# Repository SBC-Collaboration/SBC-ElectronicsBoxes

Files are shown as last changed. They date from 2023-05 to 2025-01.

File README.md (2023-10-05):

This repository contains KiCAD drawings for the LED driver PCB design, LED driver box connections, and DIO box connections. It also has the SolidWorks drawings for the panel cutouts in those boxes for CNC machining.

## LED driver
This PCB design is for driving the LED rings at 100FPS with 1A current. Each board will be able to drive 20 IR LEDs (LZ1-00R402-0000) in series. The wiring into the PCB is connectorized, so if a board fails, it can be fixed by plugging into the backup board. The op-amp is also installed onto a DIP8 daughter board, so switching a burned-out op-amp does not require soldering in the box. 
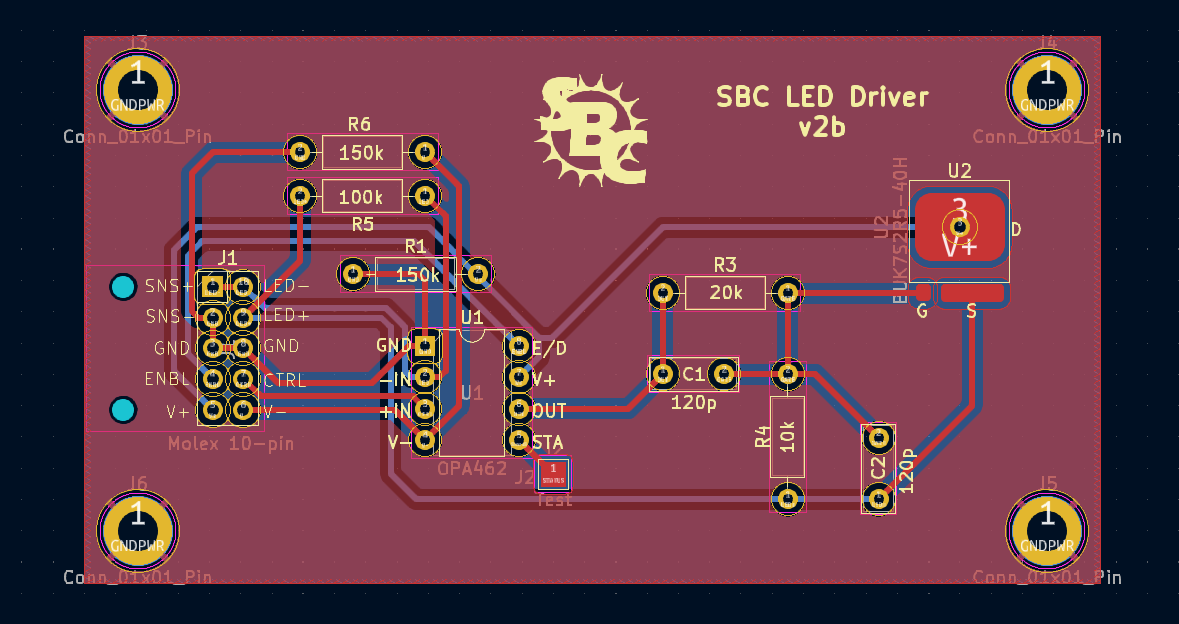
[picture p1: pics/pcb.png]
LED driver PCB

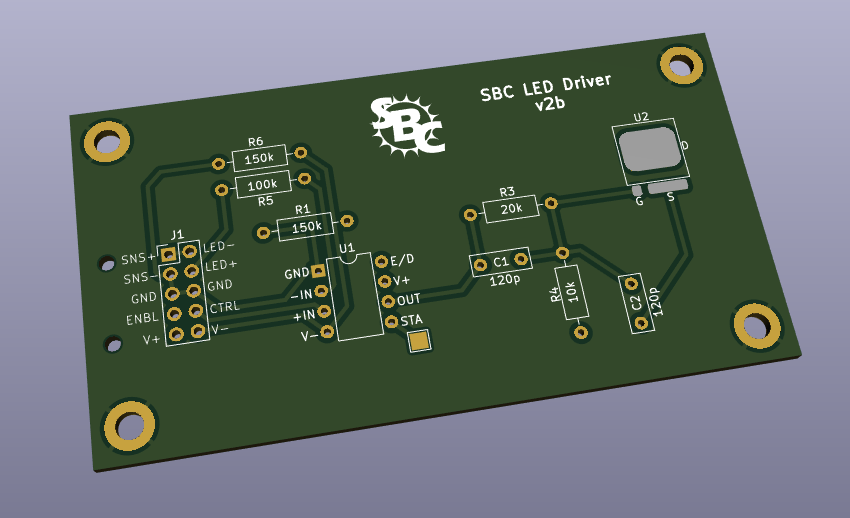
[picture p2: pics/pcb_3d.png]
LED driver PCB 3D


## LED driver box
Three PCB boards drive one LED ring, consisted of 57 LEDs total (19 in each segment). There are three sets of boards in the box, corresponding to three LED rings, plus one backup board. Three 48V 3A power supplies each power one LED ring (three boards). Clock signals from the DIO box and the control voltage pins from the PLC go through DB15 and DB9 connectors, respectively. All digital grounds are connected together, but not necessarily shared with the chassis ground (because of the painted panels). Each LED segment is connected in series with a 1 Ohm power resistor that can be used to sense the current, and also protects the LEDs inside the chamber. On the back, each LED uses a 6-pin amphenol connector, one power and one return pins for each of the LED segments. 

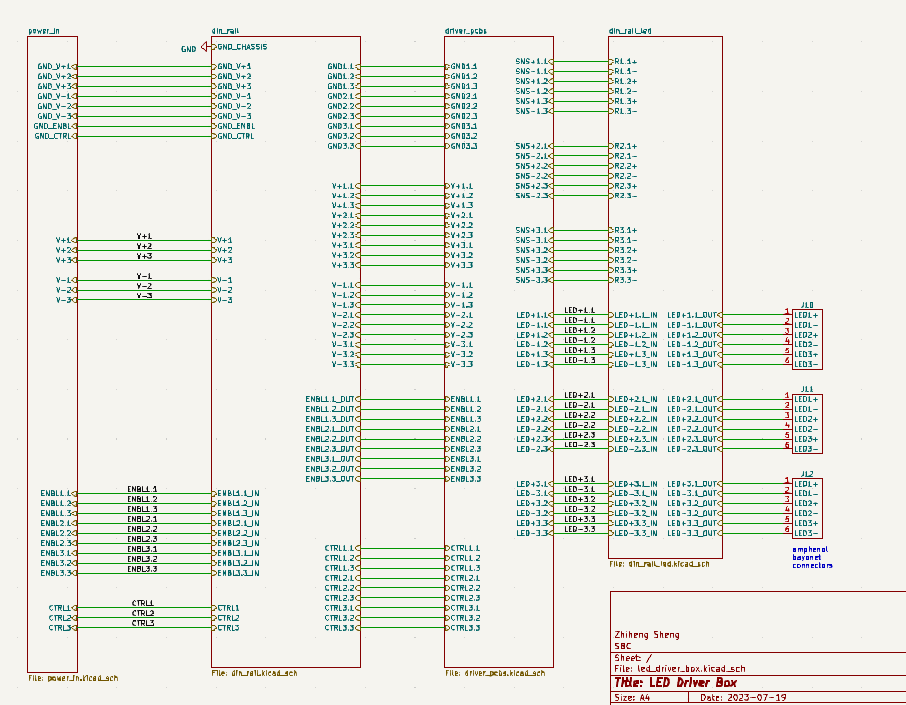
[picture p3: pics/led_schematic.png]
LED box schematics

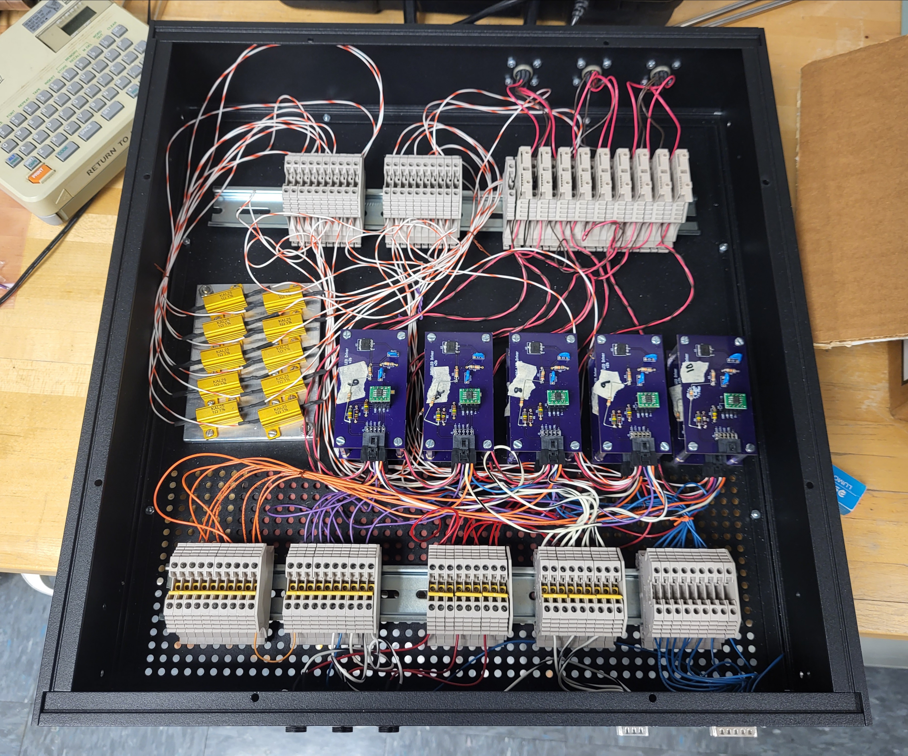
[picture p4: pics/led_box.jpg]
LED box

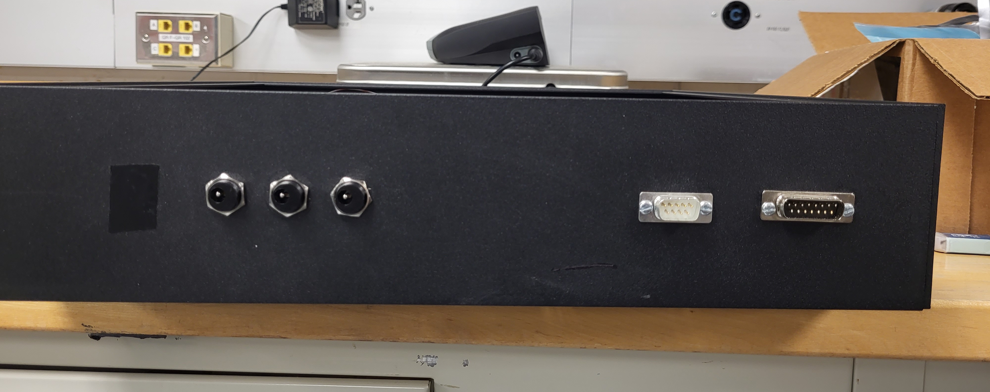
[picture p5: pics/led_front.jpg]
LED box front panel

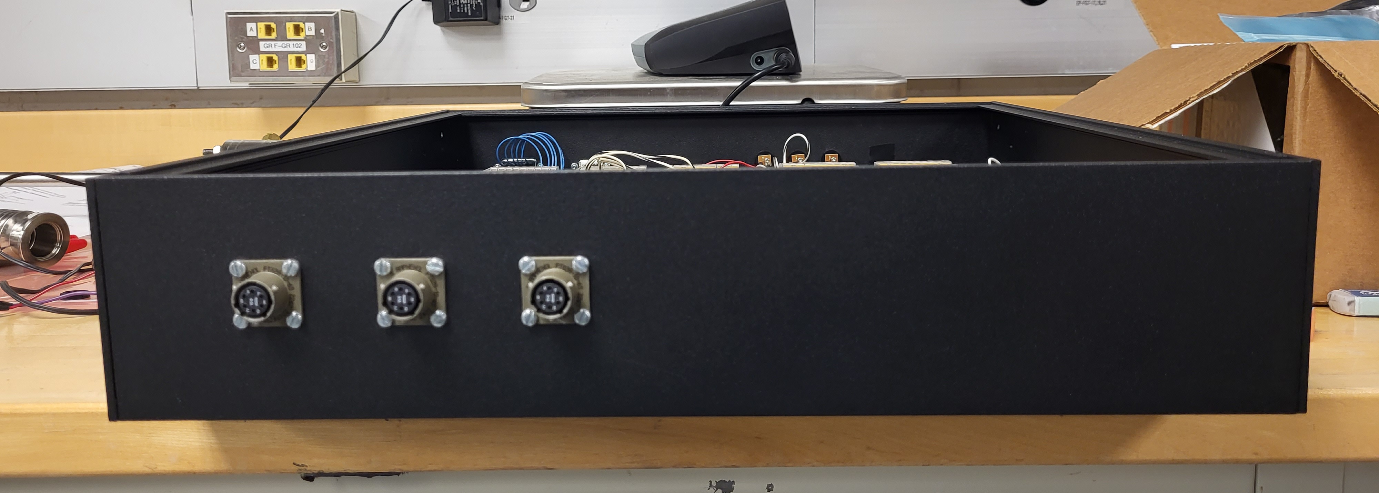
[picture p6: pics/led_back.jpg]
LED box back panel


## Digital I/O box
The DIO box is the central hub for all logic signals, including triggers, clocks, and camera controls. The back panel has four power supply jacks, each rated for 5V 3A. Three are passed through DB9s on the front panel to power the RPis for cameras, and one is used to power the USB hub. A USB jack on the back is connected to the hub, which in turn powers the three Arduinos and one NI USB device. One Arduino is responsible for trigger fan-in/fan-out. It takes trigger in and out from the 16 lemo connectors and the three camera DB9s on the front, as well as through the PLC DB9 on the back, and from the NI device from run control. The trigger reset signal comes from the NI device as well. THe clock Arduino sends clock out through the camera clock DB9 on the back, and also LED DB15 on the front. Another Ethernet jack is plugged into the ethernet shield on the Arduino for bellow position sensing. Two lemo connectors with isolated grounds are used for the sensing line for the position sensor, while the pulse signals are sent through the PLC DB9. Inside the box all digital grounds are connected together, and logic level converter or voltage divider is used for converting voltage between 3.3V(RPi), 5V (NI,Arduino,etc), and 24V (PLC). 

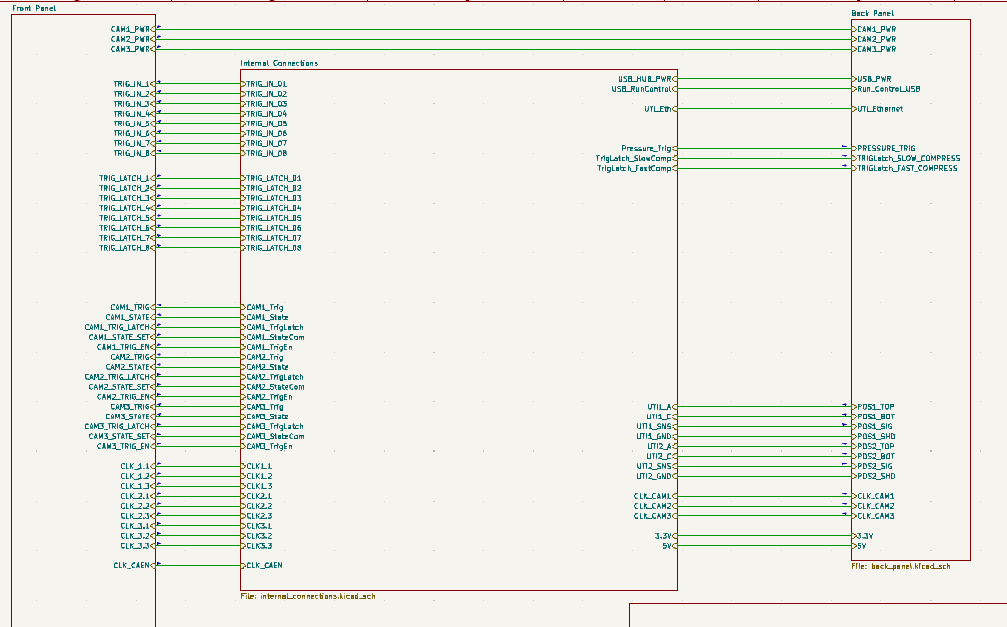
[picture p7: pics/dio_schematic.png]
DIO box schematic

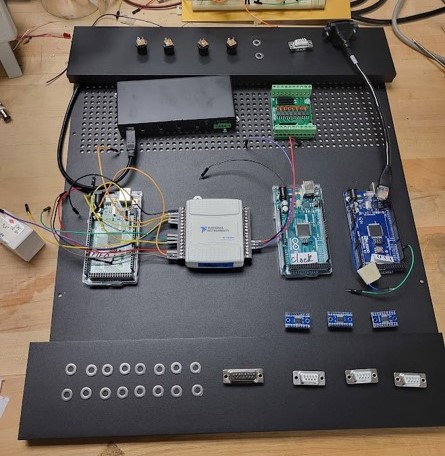
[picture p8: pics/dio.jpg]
DIO box


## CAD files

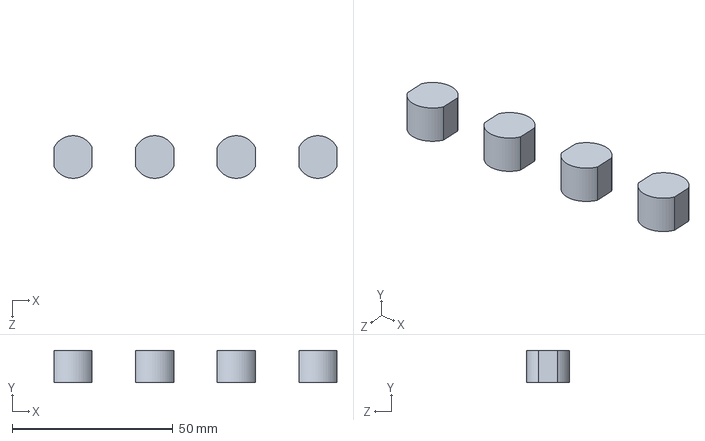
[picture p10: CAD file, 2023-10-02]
connector cutouts/barrel_dio.SLDASM
88.1 x 10.0 x 13.3 mm
barrel x 4

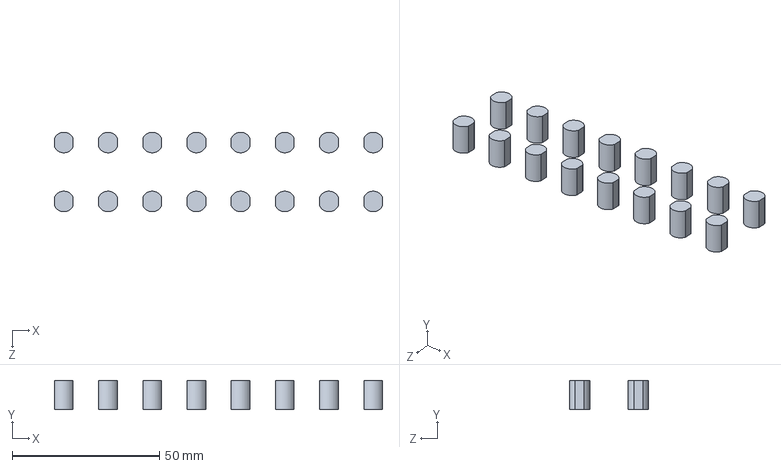
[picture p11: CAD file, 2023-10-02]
connector cutouts/lemo_cutouts.SLDASM
111.4 x 10.0 x 27.0 mm
lemo x 16

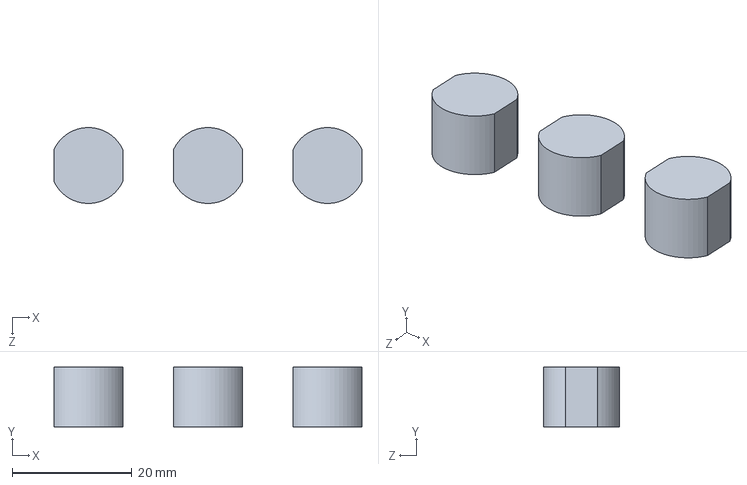
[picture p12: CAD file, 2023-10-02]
connector cutouts/barrel assem.SLDASM
51.5 x 10.0 x 12.7 mm
barrel x 3

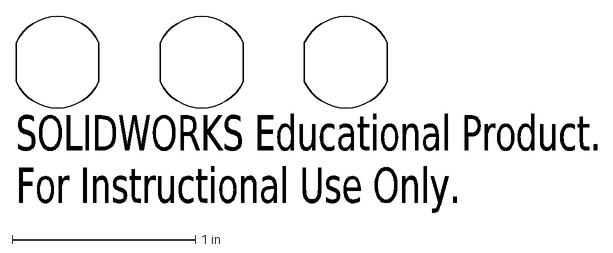
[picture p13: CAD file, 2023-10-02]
connector cutouts/CNC drawings/barrelinch.DXF
SOLIDWORKS Educational Product.
For Instructional Use Only.

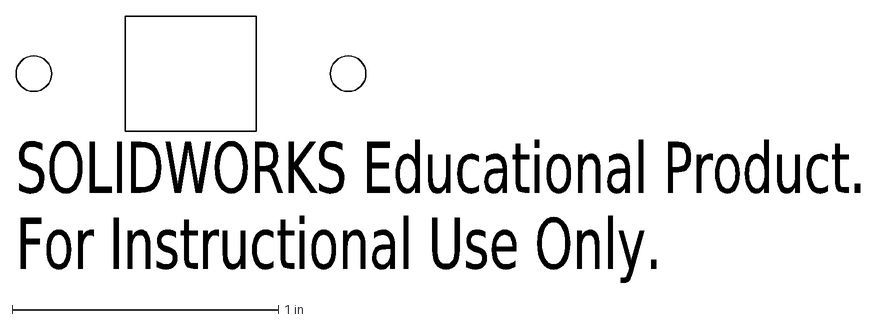
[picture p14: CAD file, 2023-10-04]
connector cutouts/DIO CNC/USBin.DXF
SOLIDWORKS Educational Product.
For Instructional Use Only.

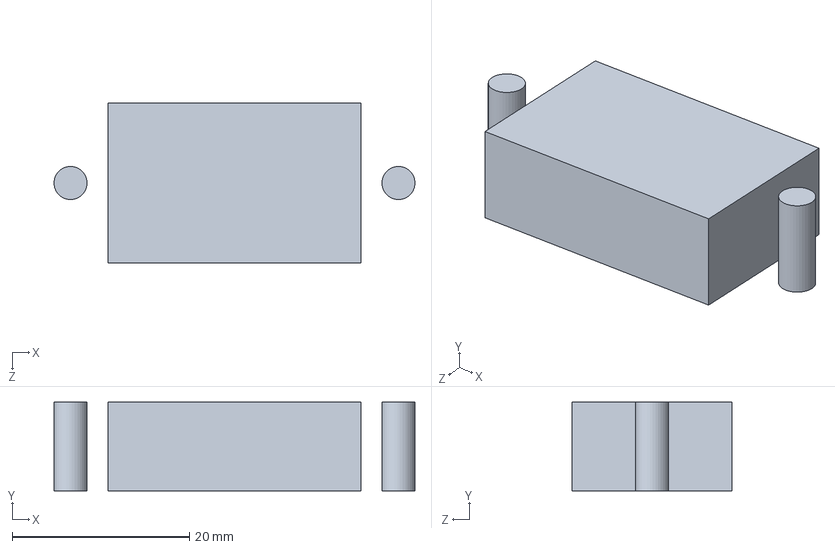
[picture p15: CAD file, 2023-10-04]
connector cutouts/Eth connector.SLDPRT
40.7 x 10.0 x 18.0 mm

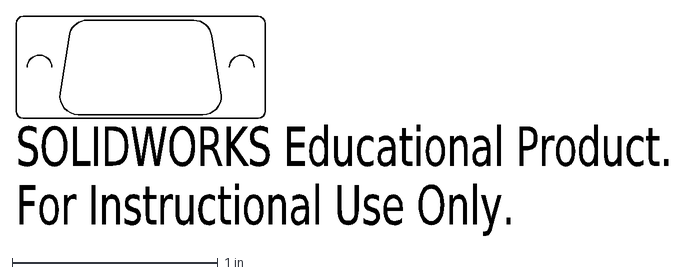
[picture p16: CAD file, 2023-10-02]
connector cutouts/CNC drawings/db9reverseinch.DXF
SOLIDWORKS Educational Product.
For Instructional Use Only.

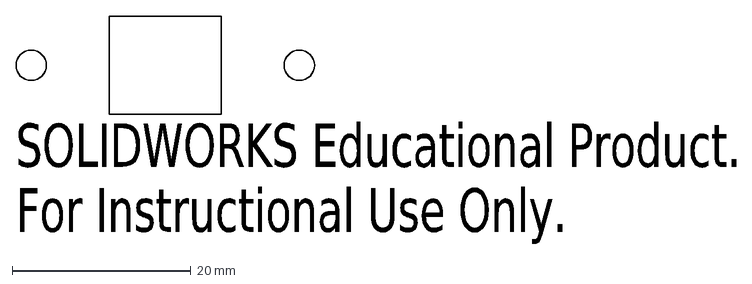
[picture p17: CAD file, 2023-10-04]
connector cutouts/DIO CNC/USBmm.DXF
SOLIDWORKS Educational Product.
For Instructional Use Only.

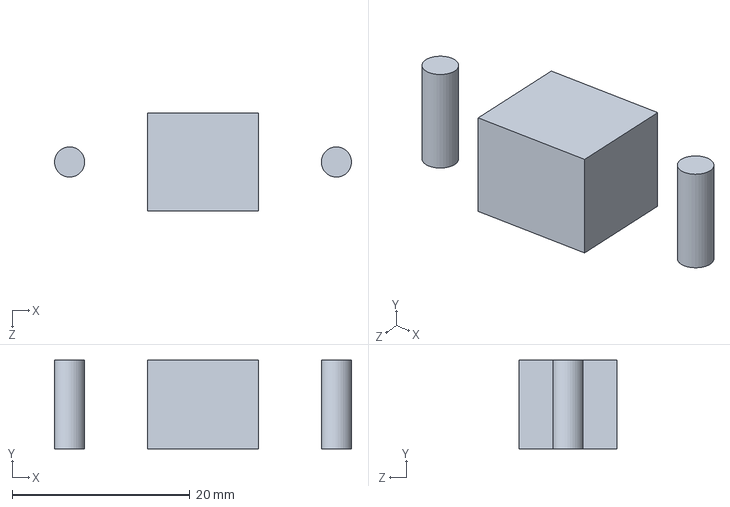
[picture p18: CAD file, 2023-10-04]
connector cutouts/USB connector.SLDPRT
33.4 x 10.0 x 11.0 mm

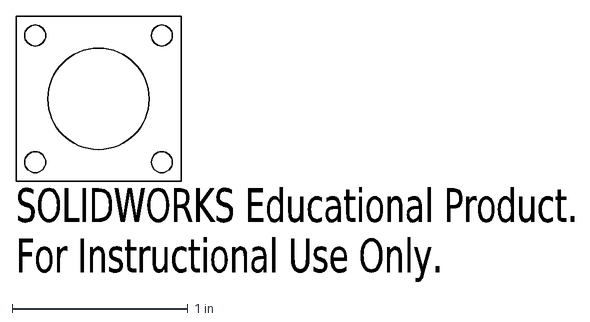
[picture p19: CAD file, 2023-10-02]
connector cutouts/CNC drawings/amphenol inch.DXF
SOLIDWORKS Educational Product.
For Instructional Use Only.

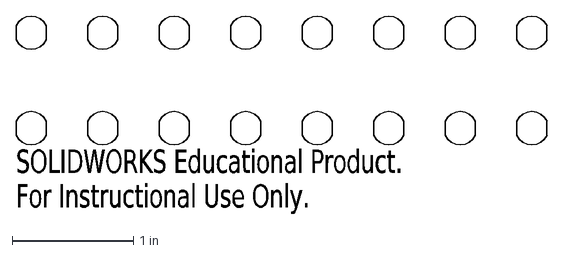
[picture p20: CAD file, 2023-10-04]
connector cutouts/DIO CNC/lemo_in.DXF
SOLIDWORKS Educational Product.
For Instructional Use Only.

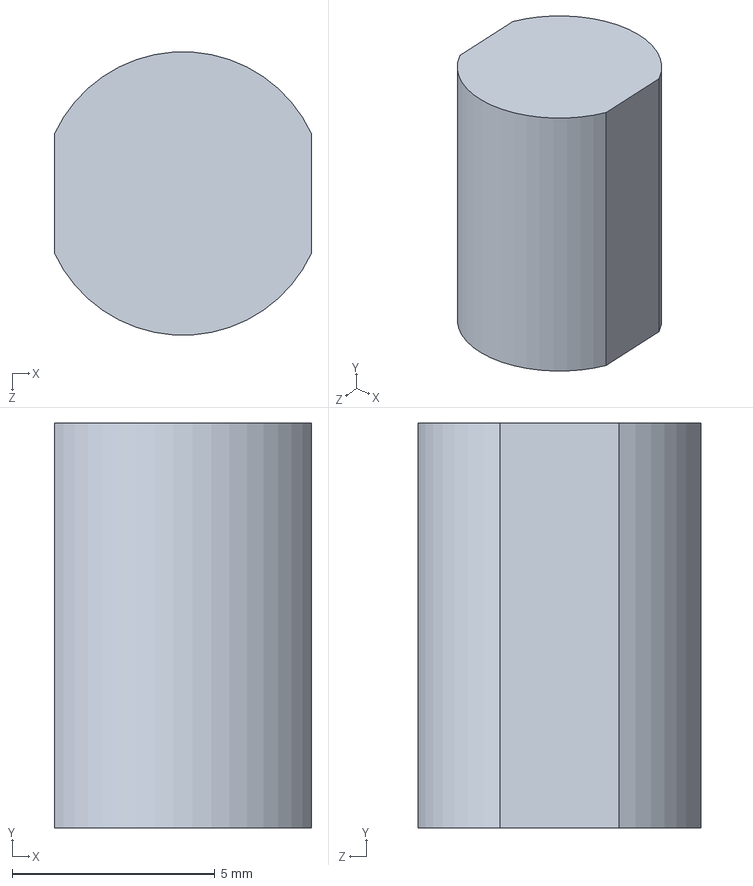
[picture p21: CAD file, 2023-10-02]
connector cutouts/lemo.SLDPRT
6.35 x 10.0 x 6.98 mm

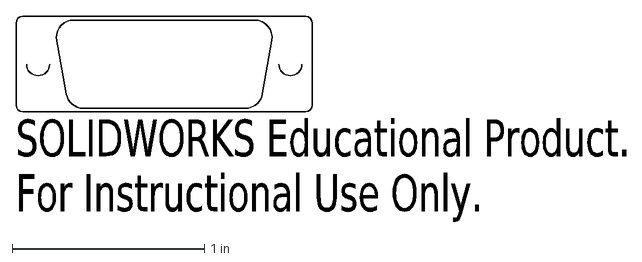
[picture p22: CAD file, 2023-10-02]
connector cutouts/CNC drawings/db15inch.DXF
SOLIDWORKS Educational Product.
For Instructional Use Only.

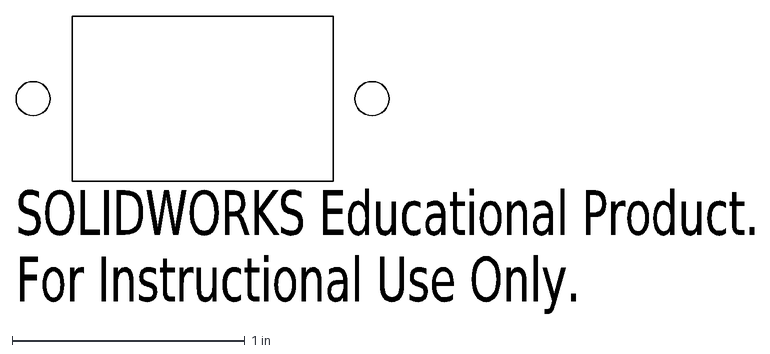
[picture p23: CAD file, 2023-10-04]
connector cutouts/DIO CNC/ETH_in.DXF
SOLIDWORKS Educational Product.
For Instructional Use Only.

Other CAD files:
connector cutouts/CNC drawings/db9reverse.DXF
connector cutouts/DIO CNC/ETH_mm.DXF
connector cutouts/barrel.SLDPRT
connector cutouts/CNC drawings/db15reverse.DXF
connector cutouts/171-009-103.STEP
connector cutouts/171-009-103.step.SLDPRT
connector cutouts/171-015-103.SLDPRT
connector cutouts/171-015-103.STEP
connector cutouts/CNC drawings/171-009-103.step.DXF
connector cutouts/CNC drawings/171-015-103.DXF
connector cutouts/CNC drawings/barrels.DXF
connector cutouts/CNC drawings/db9inch.DXF
connector cutouts/CNC drawings/three amphenol inch.DXF
connector cutouts/DIO CNC/barrel_dio_in.DXF
connector cutouts/DIO CNC/barrel_dio_mm.DXF
connector cutouts/DIO CNC/lemo_mm.DXF
connector cutouts/amphenol cutout.SLDPRT
connector cutouts/barrel assem.SLDPRT
connector cutouts/barrel assem_old.SLDPRT
connector cutouts/barrel_dio.SLDPRT
connector cutouts/barrel_old.SLDPRT
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

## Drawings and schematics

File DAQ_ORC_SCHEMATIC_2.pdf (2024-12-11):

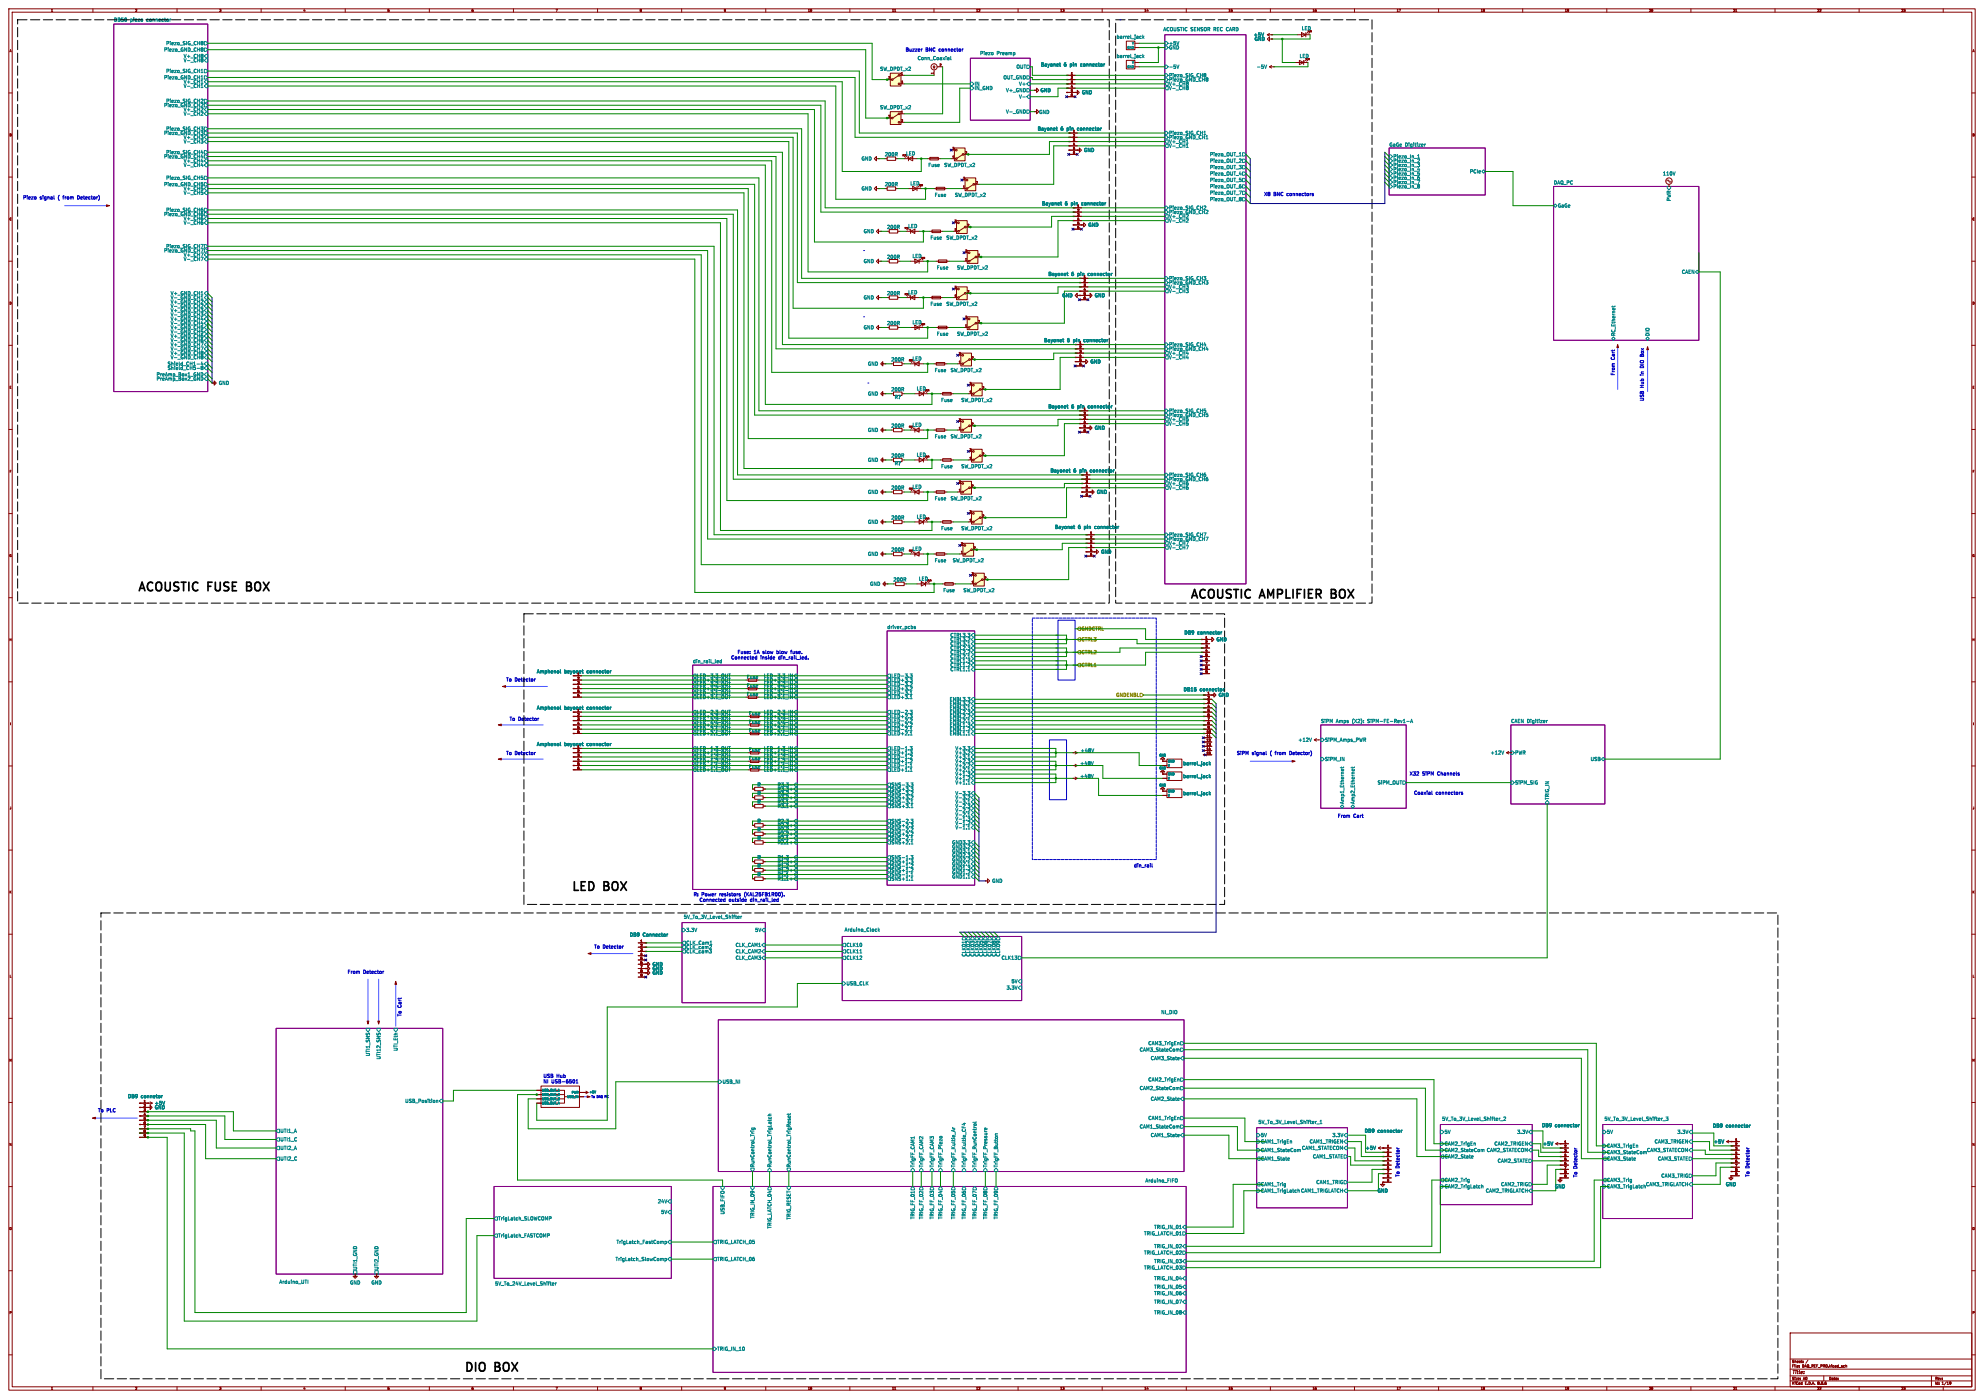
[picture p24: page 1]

ACOUSTIC SENSOR REC CARD

LED 123456 Bayonet 6 pin connector

X8 BNC connectors To Cart

Piezo signal ( from Detector)

GND 123456 Bayonet 6 pin connector

GND 123456 Bayonet 6 pin connector RR

Fuse: 1A slow blow fuse.
Connected inside din_rail_led.

Fuse 123456 Amphenol beyonet connector

Fuse 123456 Amphenol beyonet connector 123456 Amphenol beyonet connector

GND V GND GND GND Amphenol beyonet connector 123456 Amphenol beyonet connector 123456

SiPM Amps (X2): SiPM-FE-Rev1-A

SiPM signal ( from Detector)

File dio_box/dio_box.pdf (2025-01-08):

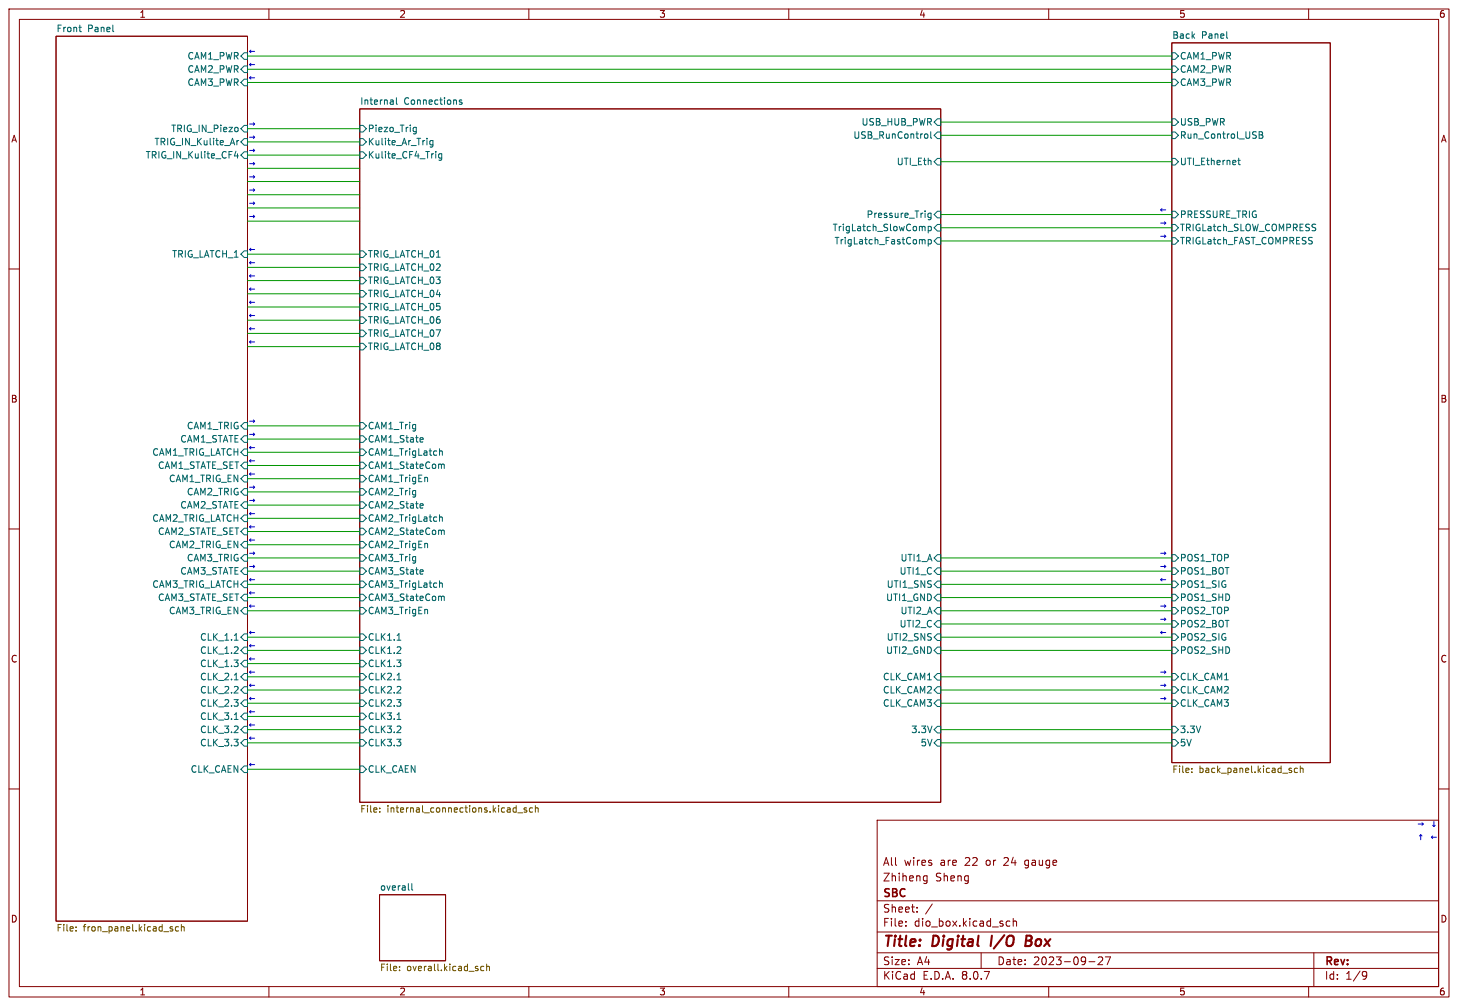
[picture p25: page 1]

Zhiheng Sheng All wires are 22 or 24 gauge

Id: 1/9 Title: Digital I/O Box

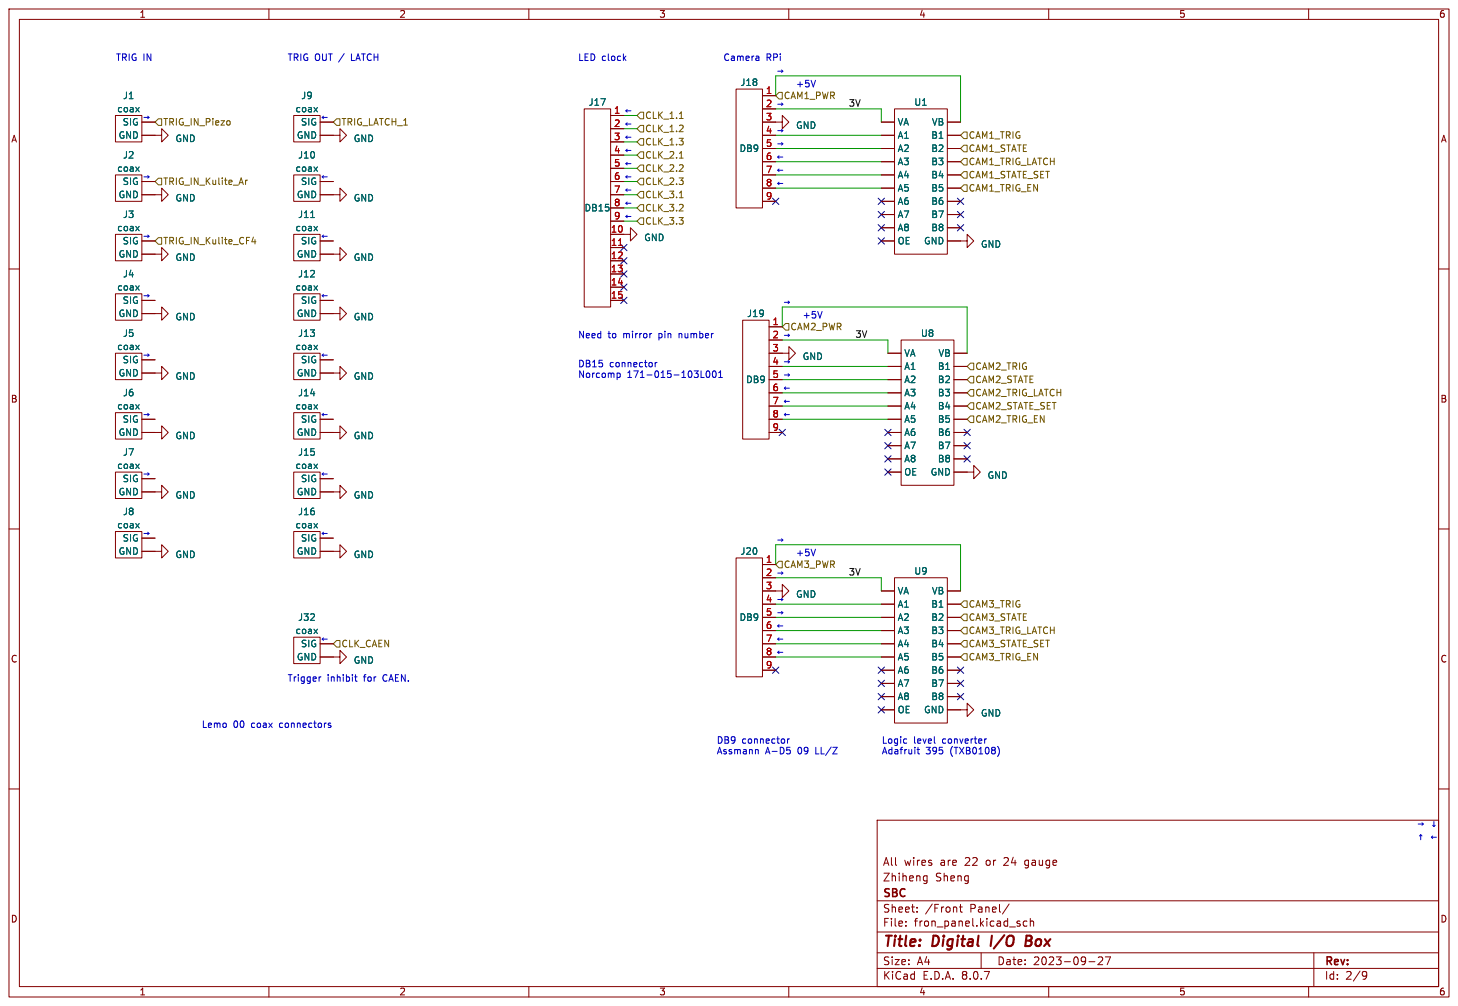
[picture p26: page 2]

þÿ!• LED clockþÿ!•
þÿ!’ DB9 connector Assmann A-D5 09 LL/Z

SIG
Zhiheng Sheng All wires are 22 or 24 gauge GND GND GND
GND

Id: 2/9 Title: Digital I/O Box

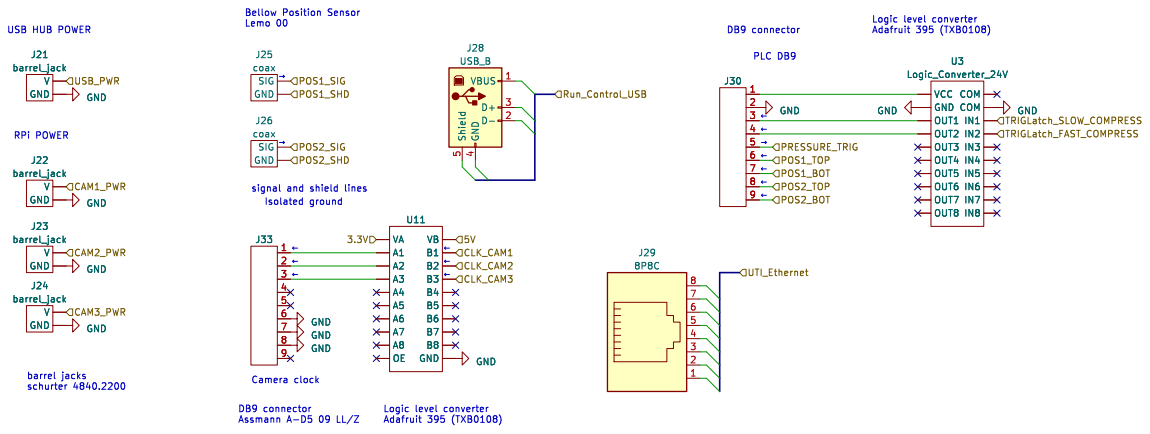
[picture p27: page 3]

þÿ!• DB9 connector þÿ!• RPi POWER

Logic level converter Adafruit 395 (TXB0108)
þÿ!• PLC DB9

þÿ!‘þÿ!• DB9 connector Assmann A-D5 09 LL/Z Camera clock þÿ!•

Zhiheng Sheng All wires are 22 or 24 gauge

Id: 3/9 Title: Digital I/O Box

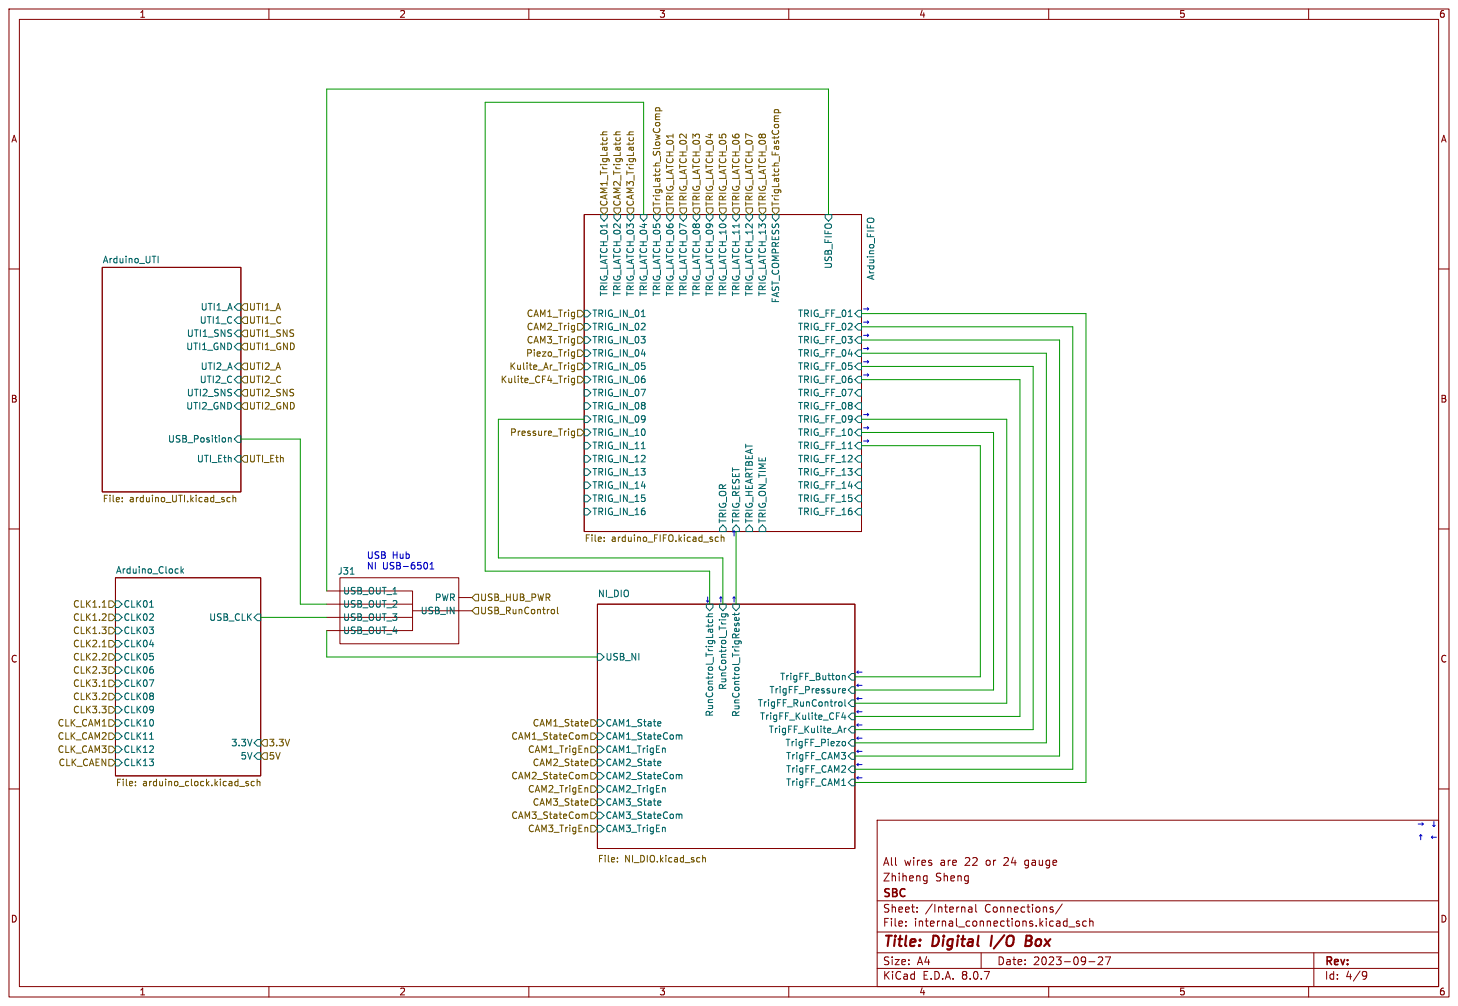
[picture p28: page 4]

þÿ!’ USB Hub NI USB-6501

Id: 4/9 Title: Digital I/O Box

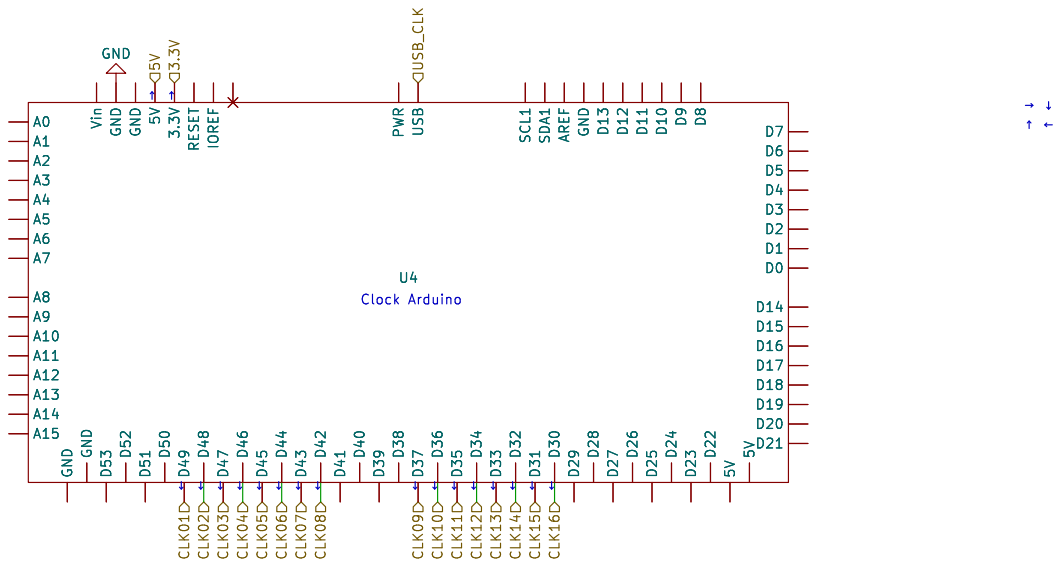
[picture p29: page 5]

þÿ!“þÿ!“ Clock Arduino

Zhiheng Sheng All wires are 22 or 24 gauge

Id: 5/9 Title: Digital I/O Box

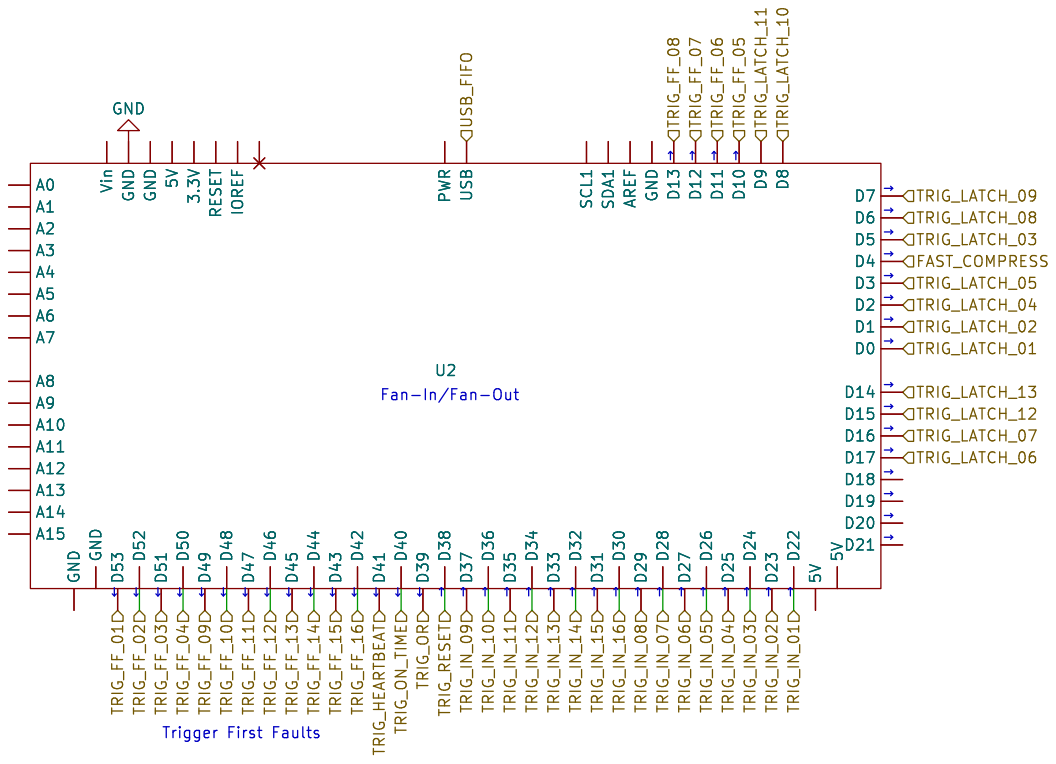
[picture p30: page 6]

Trigger First Faults þÿ!“þÿ!“

Zhiheng Sheng All wires are 22 or 24 gauge

Id: 6/9 Title: Digital I/O Box

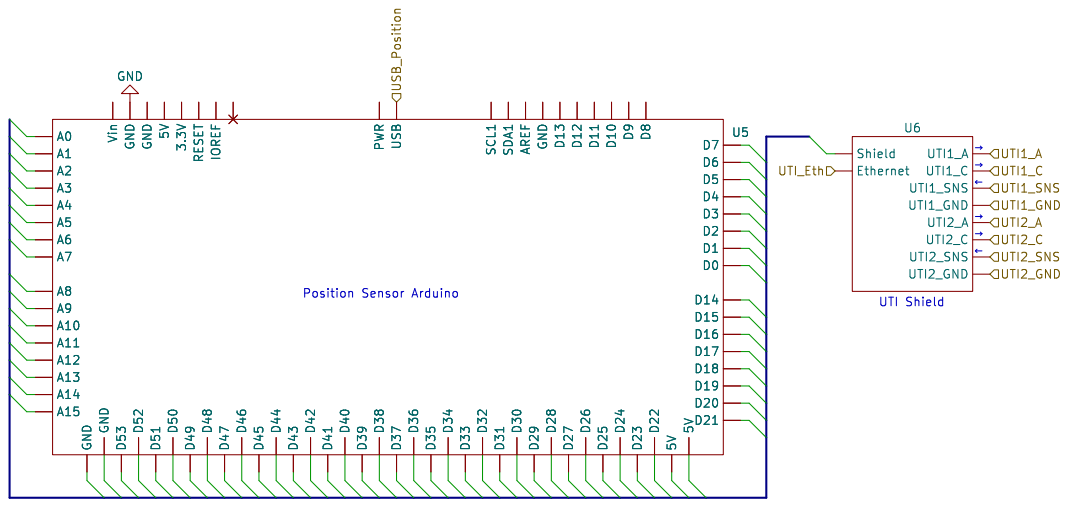
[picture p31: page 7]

Zhiheng Sheng All wires are 22 or 24 gauge

Id: 7/9 Title: Digital I/O Box

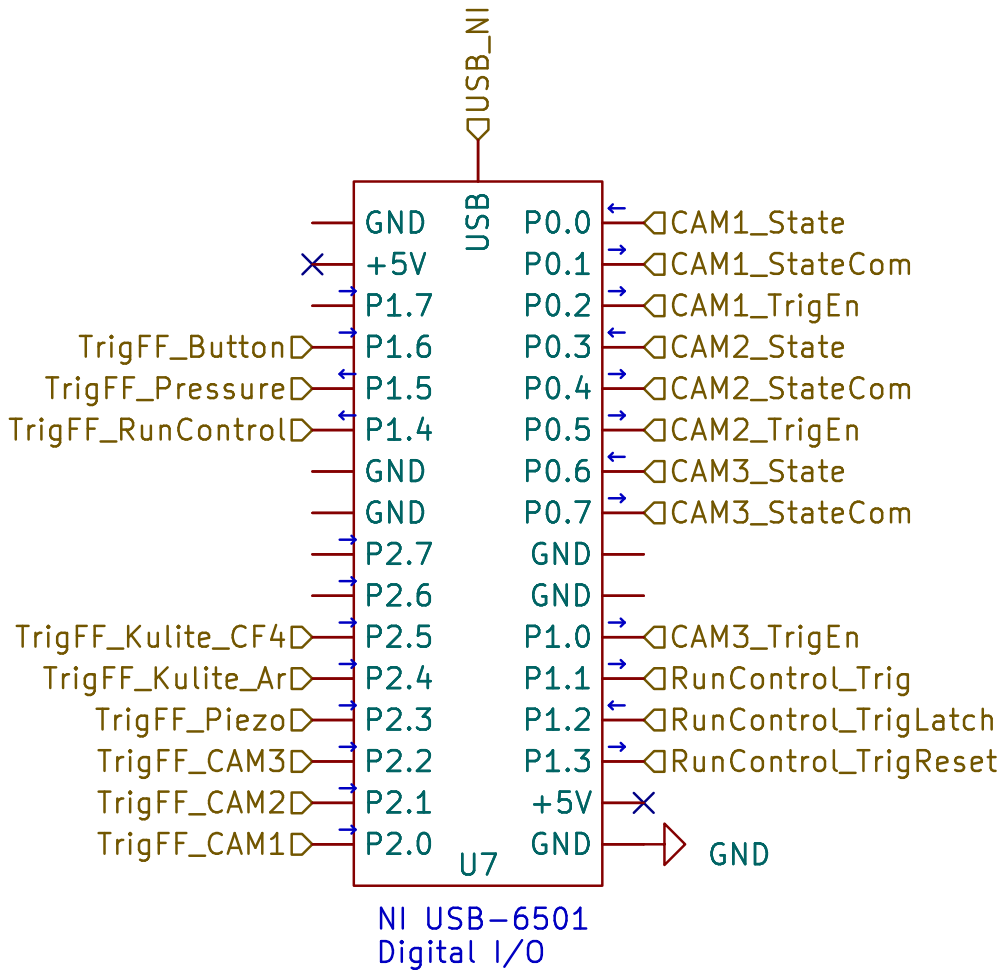
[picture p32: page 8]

Zhiheng Sheng All wires are 22 or 24 gauge

Id: 8/9 Title: Digital I/O Box

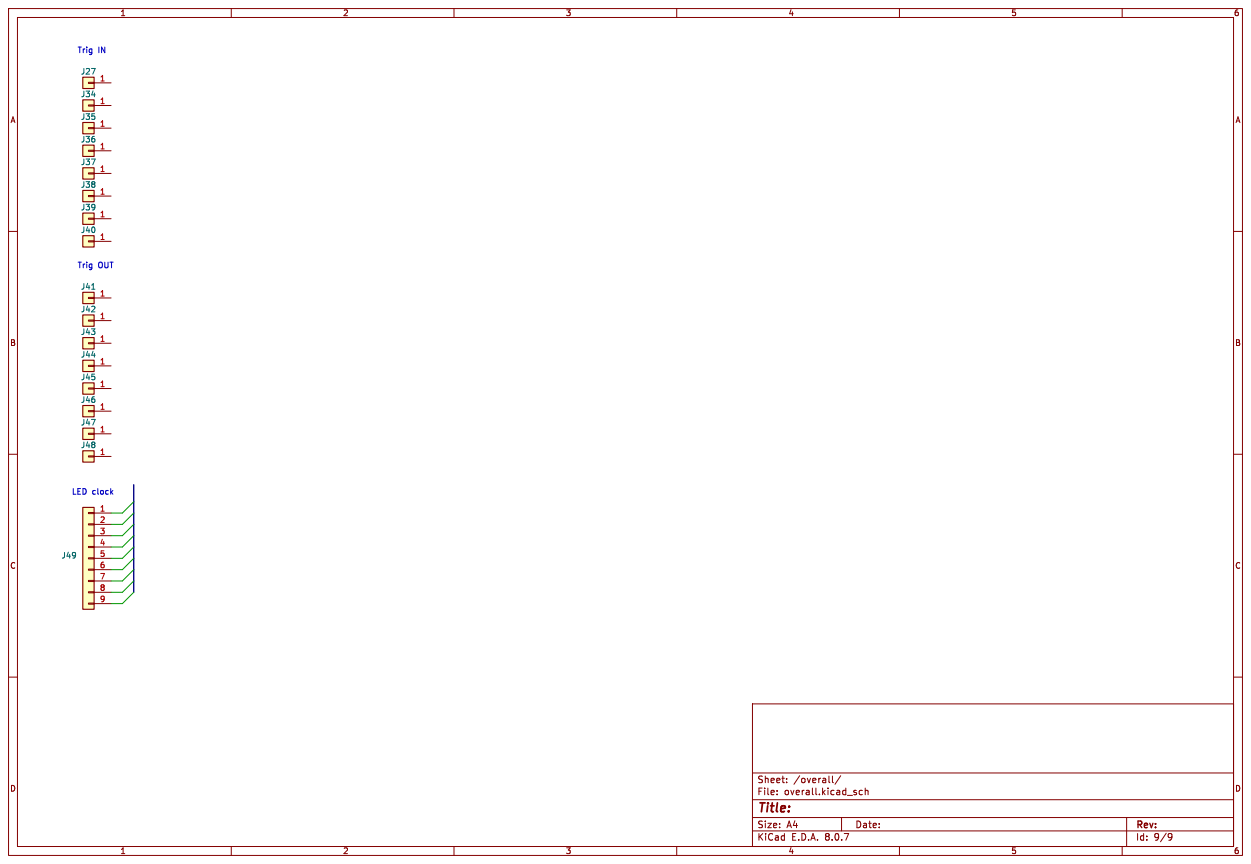
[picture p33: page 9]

Trig IN
LED clock Trig OUT

Id: 9/9 Title: File: overall.kicad_sch Sheet: /overall/ 1

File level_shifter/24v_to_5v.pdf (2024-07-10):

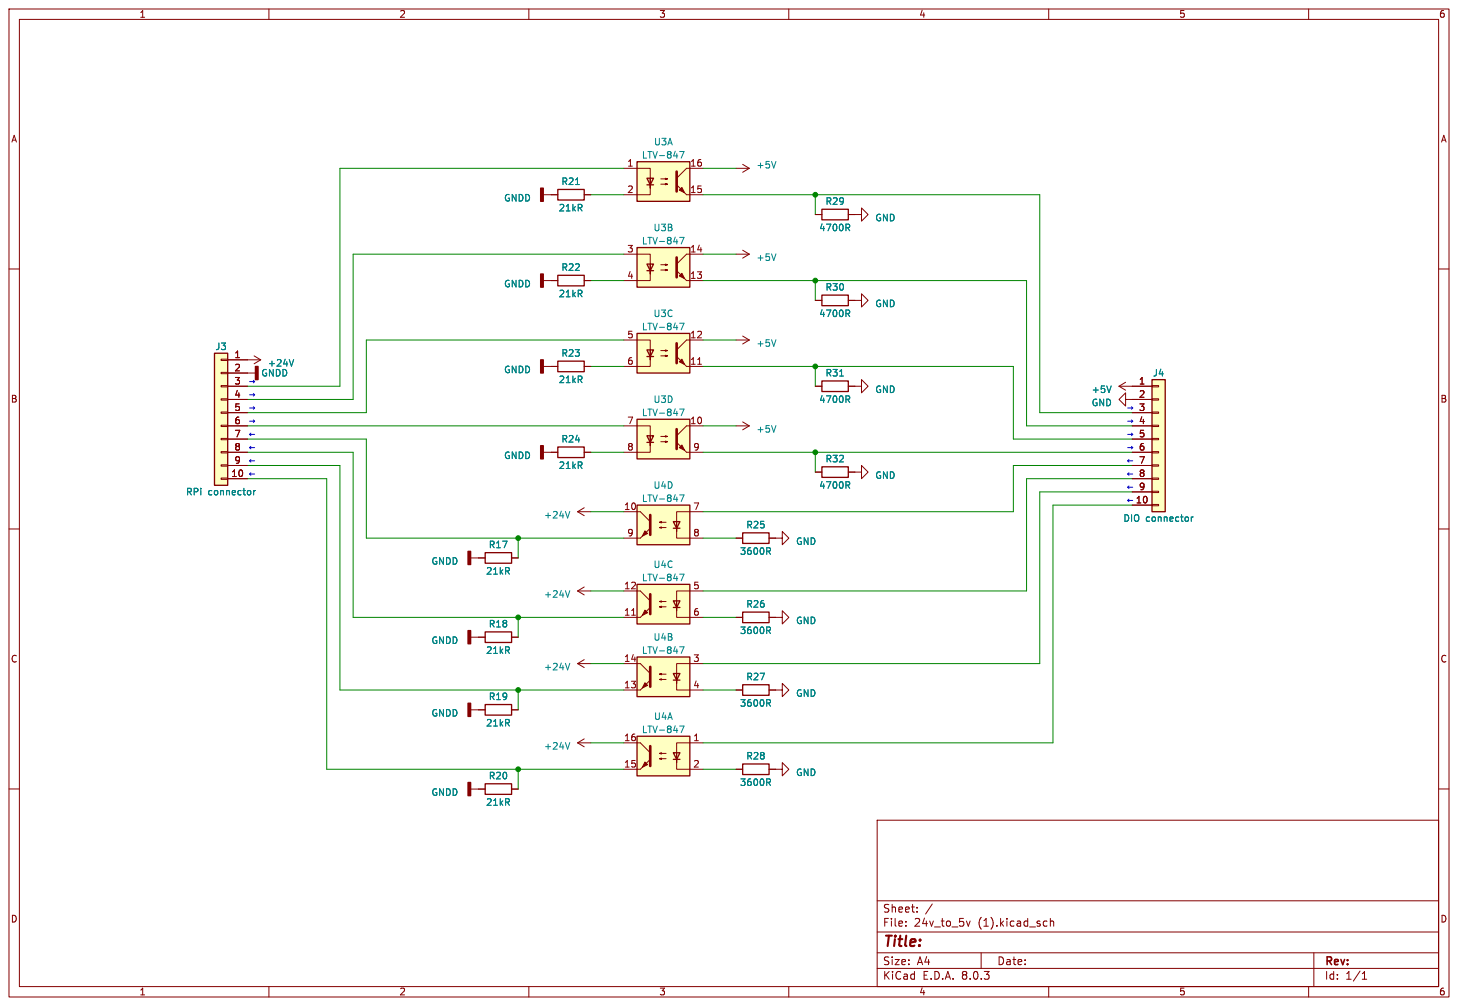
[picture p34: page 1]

21kR GNDD GNDD +24V GNDD R22 R22

þÿ!• GND GND GND

J4 DIO connector GND GND

Id: 1/1 Title: File: 24v_to_5v (1).kicad_sch Sheet: / 13

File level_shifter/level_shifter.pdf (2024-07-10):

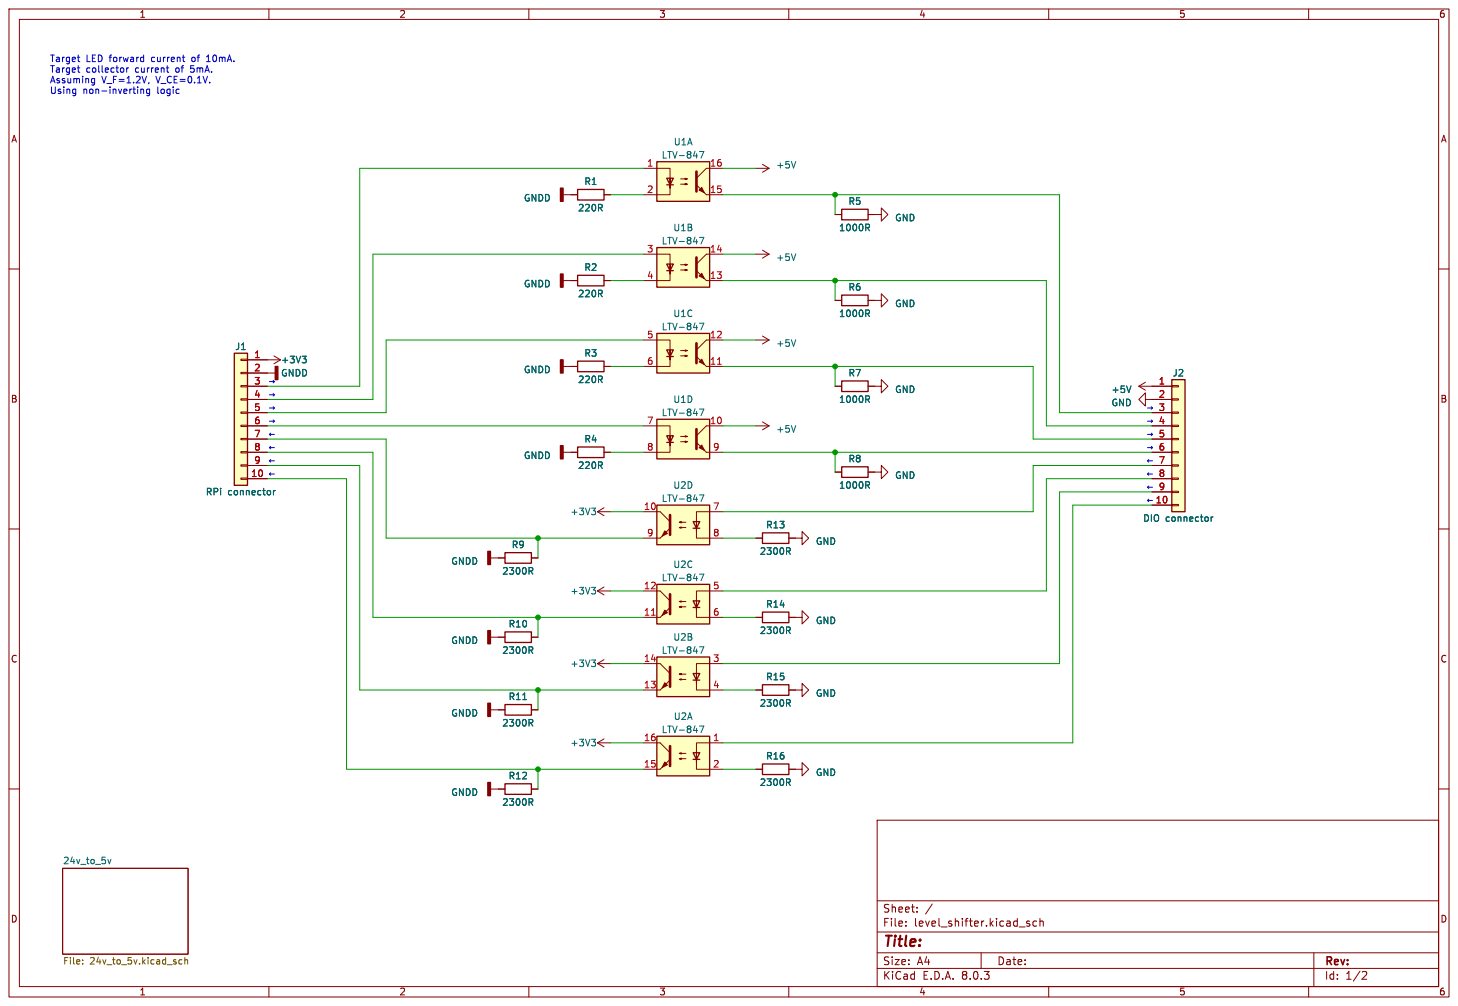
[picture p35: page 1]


21kR GNDD +24V GNDD R22

Id: 2/2 Title: File: 24v_to_5v.kicad_sch Sheet: /24v_to_5v/

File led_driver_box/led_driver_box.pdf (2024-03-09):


Id: 1/14 Title: LED Driver Box


Id: 2/14 Title: LED Driver Box


LED- driver_pcb3.1 File: driver_pcb.kicad_sch V- CTRL GND
LED- driver_pcb1.3 File: driver_pcb.kicad_sch V- CTRL GND

LED+2.2 V-1.1 SNS+1.1 SNS-1.1 ENBL1.1 V+1.1 SNS-1.2 ENBL1.2 V+1.2 SNS+1.2 SNS-1.3 V+1.3 ENBL1.3 SNS+1.3

LED+ SNS+ SNS- ENBL V+GND_NC

LED- driver_pcb1.2 File: driver_pcb.kicad_sch V- CTRL GND

LED- driver_pcb3.2 File: driver_pcb.kicad_sch V- CTRL GND

LED- driver_pcb3.3 File: driver_pcb.kicad_sch V- CTRL GND

Id: 3/14 Title: LED Driver Box


Id: 4/14 Title: LED Driver Box


Id: 5/14 Title: LED Driver Box










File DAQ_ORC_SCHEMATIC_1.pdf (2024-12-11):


Id: 1/13 Title: SBC Electronics Overall File: final_overall.kicad_sch Sheet: /

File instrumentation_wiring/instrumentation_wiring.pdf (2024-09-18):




(Buzzer or input) DPDT switch
for CH1





Zhiheng Sheng
File: switch.kicad_sch Sheet: /Cart/Switch/ SBC




Zhiheng Sheng
File: vj_feedthroughs.kicad_sch Sheet: /VJ feedthroughs/ SBC



CAEN Digitizer CAEN GaGe DIO

Zhiheng Sheng
File: rack.kicad_sch Sheet: /Rack/ SBC


PLC UPS DAQ UPS PLC PC

Zhiheng Sheng
File: cart.kicad_sch Sheet: /Cart/ SBC


Zhiheng Sheng
File: plc.kicad_sch Sheet: /PLC/ SBC




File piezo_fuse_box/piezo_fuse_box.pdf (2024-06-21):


Id: 1/5 Title: Piezo fuse box


Id: 2/5 Title: Piezo fuse box


Id: 3/5 Title: Piezo fuse box


Id: 4/5 Title: Piezo fuse box


Id: 5/5 Title: Piezo fuse box

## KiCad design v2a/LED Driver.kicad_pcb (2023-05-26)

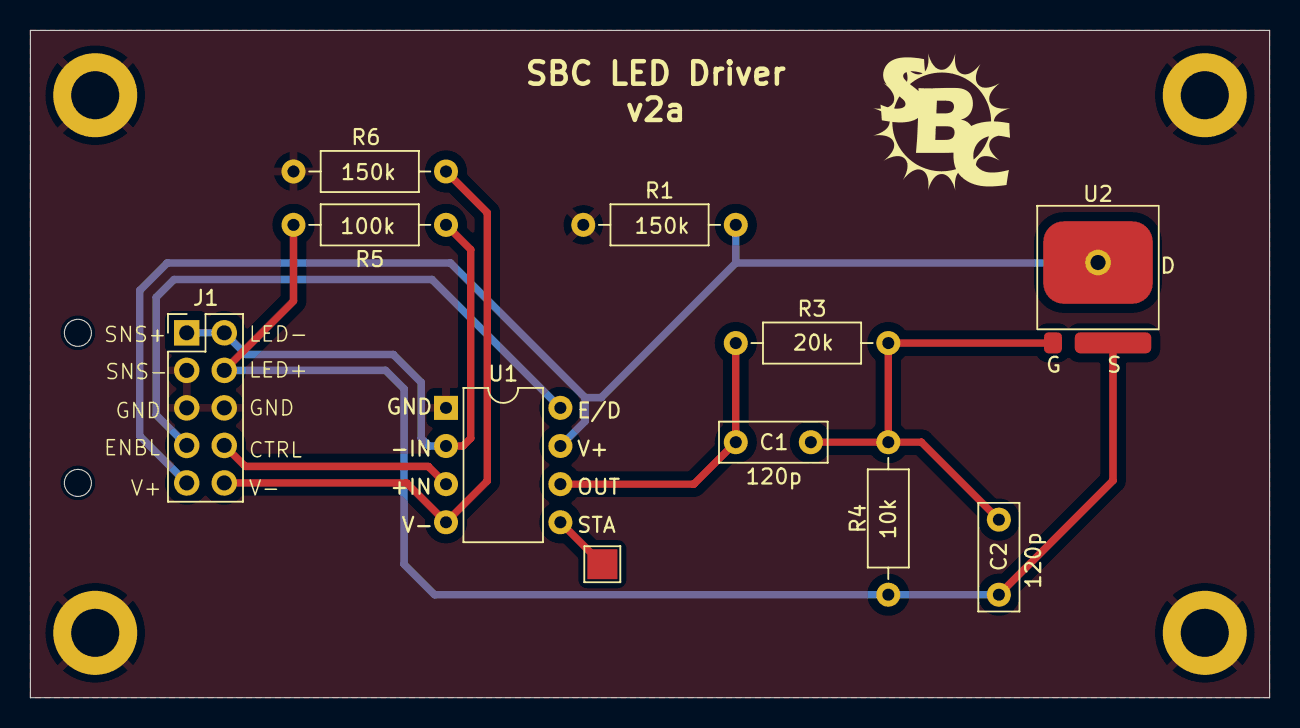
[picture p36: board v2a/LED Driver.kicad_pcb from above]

Board: 2 copper layers, 82.5 x 44.4 mm, 15 parts (0 on the bottom side), 10 nets.

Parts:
C1, C2: 120p; C_Disc_D7.0mm_W2.5mm_P5.00mm
J1: Molex 10-pin; PinHeader_2x05_P2.54mm_Vertical
J2: Test; TestPoint_Pad_2.0x2.0mm
J3, J4, J5, J6: Conn_01x01_Pin; MountingHole_3.2mm_M3_DIN965_Pad
R1, R6: 150k; R_Axial_DIN0207_L6.3mm_D2.5mm_P10.16mm_Horizontal
R3: 20k; R_Axial_DIN0207_L6.3mm_D2.5mm_P10.16mm_Horizontal
R4: 10k; R_Axial_DIN0207_L6.3mm_D2.5mm_P10.16mm_Horizontal
R5: 100k; R_Axial_DIN0207_L6.3mm_D2.5mm_P10.16mm_Horizontal
U1: OPA462; DIP-8_W7.62mm
U2: BUK7S2R5-40H; BUK7S2R5-40H_footprint

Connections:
/CTRL: J1.7 (CTRL), U1.3 (+IN)
/ENBL: J1.4 (ENBL), U1.8 (E/D)
/GATE: C1.2, C2.2, R3.1, R4.2
/LED+: C2.1, J1.9 (LED+), R4.1, R5.2
/LED-: J1.1 (SNS+), J1.10 (LED-), R5.1, U1.2 (-IN)
/OUT: C1.1, R3.2, U1.6 (OUT)
/STATUS: J2.1, U1.5 (Status)
/V+: J1.5 (V+), R1.2, U1.7 (V+)
/V-: J1.6 (V-), R6.1, U1.4 (V-)
GND: J1.2 (SNS-), J1.3 (GND), J1.8 (GND), J3.1, J4.1, J5.1, J6.1, R1.1, R6.2, U1.1 (COM)

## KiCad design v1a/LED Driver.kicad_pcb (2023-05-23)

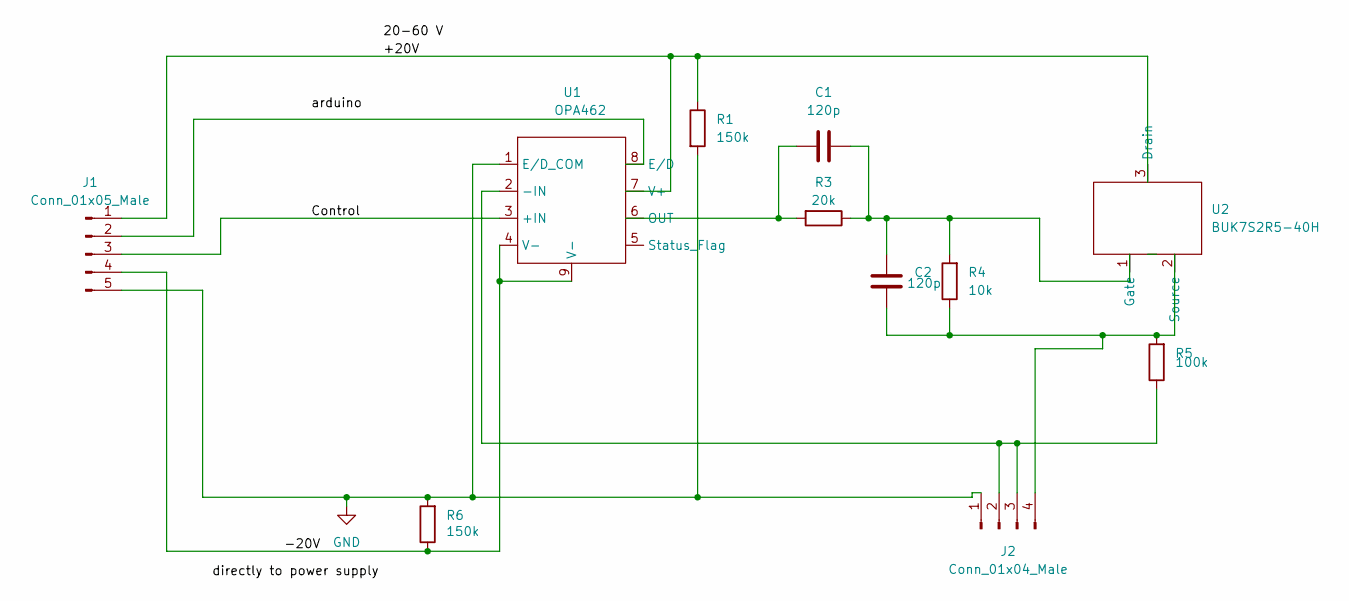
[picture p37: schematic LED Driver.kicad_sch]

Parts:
C1, C2: 120p; CP_Radial_D5.0mm_P2.50mm
J1: Conn_01x05_Male; PinHeader_1x05_P2.54mm_Vertical
J2: Conn_01x04_Male; PinHeader_1x04_P2.54mm_Vertical
R1, R6: 150k; R_Axial_DIN0207_L6.3mm_D2.5mm_P10.16mm_Horizontal
R3: 20k; R_Axial_DIN0207_L6.3mm_D2.5mm_P10.16mm_Horizontal
R4: 10k; R_Axial_DIN0207_L6.3mm_D2.5mm_P10.16mm_Horizontal
R5: 100k; R_Axial_DIN0207_L6.3mm_D2.5mm_P10.16mm_Horizontal
U1: OPA462; SOIC-8-1EP_3.9x4.9mm_P1.27mm_EP2.62x3.51mm_ThermalVias
U2: BUK7S2R5-40H; BUK7S2R5-40H_footprint

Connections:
/+20V: J1.1, R1.1, U1.7 (V+), U2.3 (Drain)
/-20V: J1.4, R6.1, U1.4 (V-), U1.9 (V-)
/Control: J1.3, U1.3 (+IN)
/arduino: J1.2, U1.8 (E/D)
GND: J1.5, J2.1, R1.2, R6.2, U1.1 (E/D_COM)
unnamed: C1.1, R3.2, U1.6 (OUT)
unnamed: C1.2, C2.2, R3.1, R4.2, U2.1 (Gate)
unnamed: C2.1, J2.4, R4.1, R5.2, U2.2 (Source)
unnamed: J2.2, J2.3, R5.1, U1.2 (-IN)

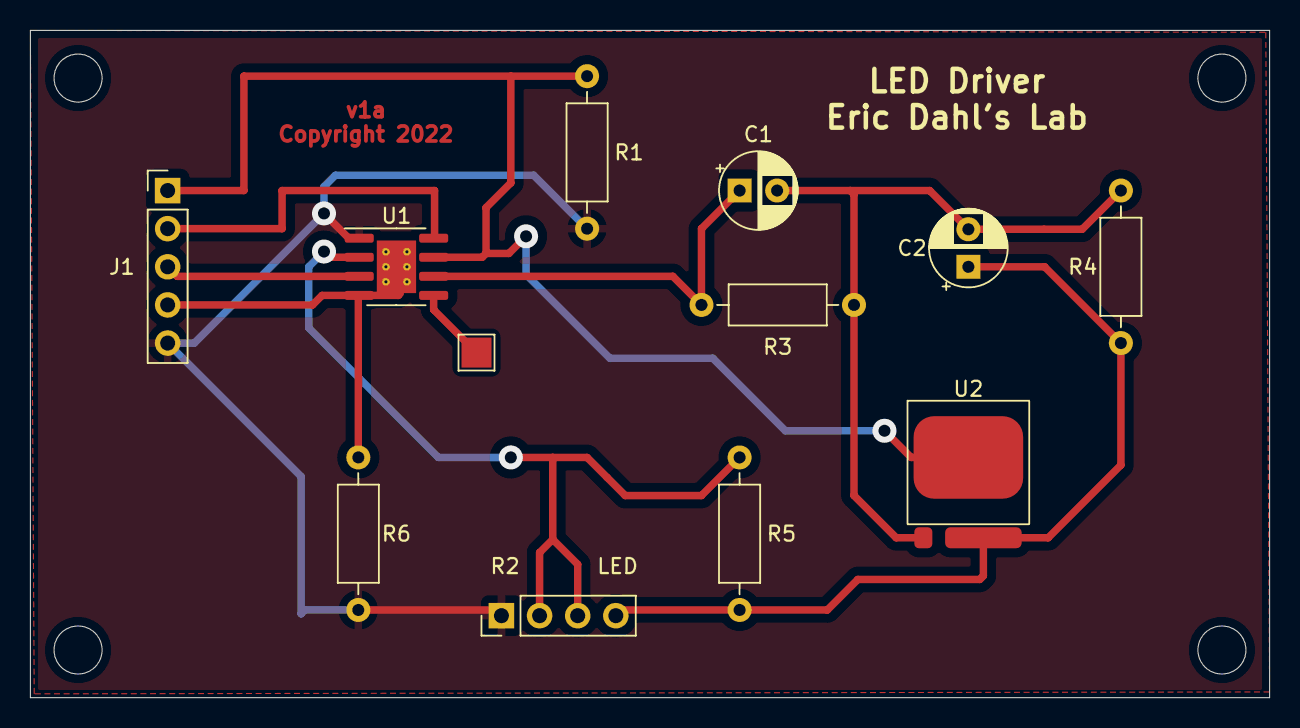
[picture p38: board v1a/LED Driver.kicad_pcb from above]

Board: 2 copper layers, 82.5 x 44.5 mm, 11 parts (0 on the bottom side), 9 nets.

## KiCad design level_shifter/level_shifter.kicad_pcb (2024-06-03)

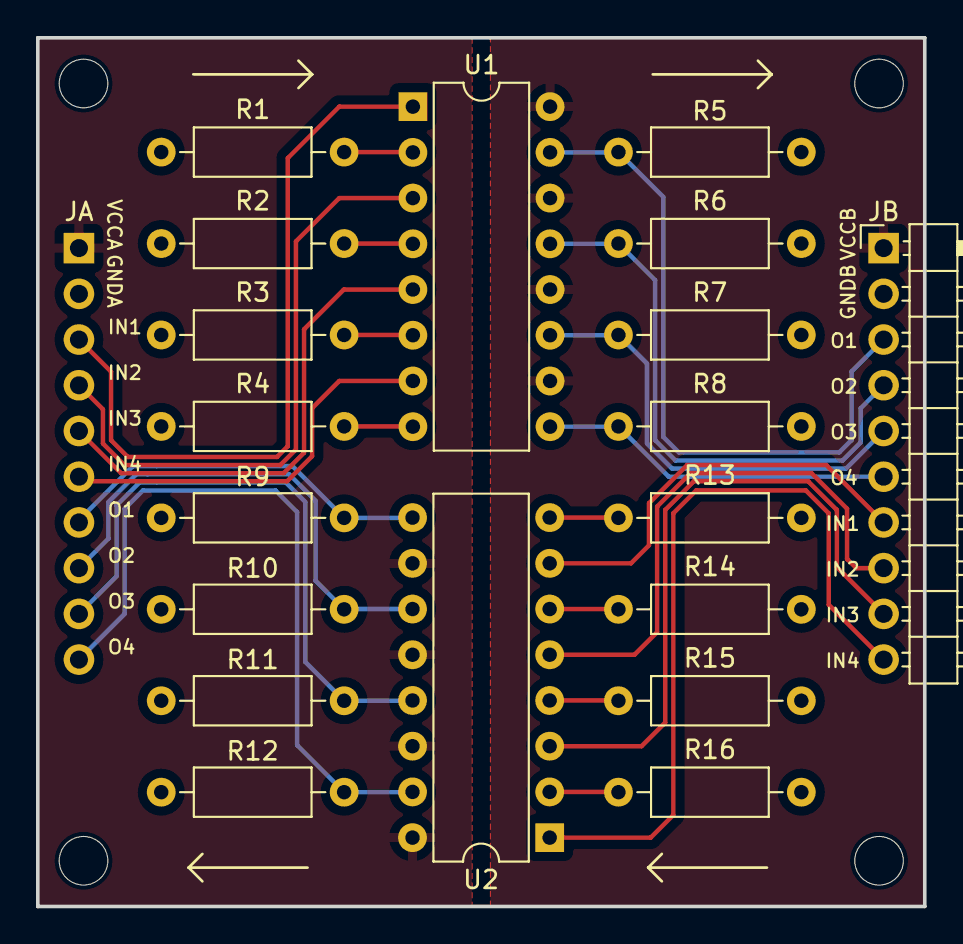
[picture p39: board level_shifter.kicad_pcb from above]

Board: 2 copper layers, 49.3 x 48.3 mm, 20 parts (1 on the bottom side), 28 nets.

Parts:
JA: RPi connector; PinHeader_1x10_P2.54mm_Horizontal
JB: DIO connector; PinHeader_1x10_P2.54mm_Horizontal
R1, R2, R3, R4: 220R; R_Axial_DIN0207_L6.3mm_D2.5mm_P10.16mm_Horizontal
R5, R6, R7, R8: 1000R; R_Axial_DIN0207_L6.3mm_D2.5mm_P10.16mm_Horizontal
R9, R10, R11, R12: 620R; R_Axial_DIN0207_L6.3mm_D2.5mm_P10.16mm_Horizontal
R13, R14, R15, R16: 390R; R_Axial_DIN0207_L6.3mm_D2.5mm_P10.16mm_Horizontal
U1, U2: LTV-847; DIP-16_W7.62mm

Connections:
+3V3: JA.1, U2.10, U2.12, U2.14, U2.16
+5V: JB.1, U1.10, U1.12, U1.14, U1.16
GND: JB.2, R5.1, R6.2, R7.2, R8.2, R13.2, R14.2, R15.2, R16.2
GNDD: JA.2, R1.1, R2.1, R3.1, R4.1, R9.1, R10.1, R11.1, R12.1
unnamed: JA.3, U1.1
unnamed: JA.4, U1.3
unnamed: JA.5, U1.5
unnamed: JA.6, U1.7
unnamed: JA.7, R9.2, U2.9
unnamed: JA.8, R10.2, U2.11
unnamed: JA.9, R11.2, U2.13
unnamed: JA.10, R12.2, U2.15
unnamed: JB.3, R5.2, U1.15
unnamed: JB.4, R6.1, U1.13
unnamed: JB.5, R7.1, U1.11
unnamed: JB.6, R8.1, U1.9
unnamed: JB.7, U2.7
unnamed: JB.8, U2.5
unnamed: JB.9, U2.3
unnamed: JB.10, U2.1
unnamed: R1.2, U1.2
unnamed: R2.2, U1.4
unnamed: R3.2, U1.6
unnamed: R4.2, U1.8
unnamed: R13.1, U2.8
unnamed: R14.1, U2.6
unnamed: R15.1, U2.4
unnamed: R16.1, U2.2

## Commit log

2023-05-23 Initial commit, completed v2a that has a molex connector and the opamp is installed onto a DIP8 carrier board. Started on schematic of driver box wiring and external wiring to the VJ
    [LED Driver-B_Cu.gbl, LED Driver-B_Mask.gbs, LED Driver-B_Paste.gbp, LED Driver-B_Silkscreen.gbo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]
2023-05-23 Clean up folder structure, add page info
    [LED Driver-B_Cu.gbl, LED Driver-B_Mask.gbs, LED Driver-B_Paste.gbp, LED Driver-B_Silkscreen.gbo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]
2023-05-26 Modified led driver box wiring
    [LED Driver.kicad_pcb, din_rail.kicad_sch, din_rail_led.kicad_sch, driver_pcb.kicad_sch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]
2023-05-30 Update to the LED driver box wiring schematic
    [driver_pcb.kicad_sch, driver_pcbs.kicad_sch]
2023-05-30 Modified to v2b version, where the copper layer on PCB is connected to chassis and mounting holes, which is separated from all electric grounds (arduino, power supply, PLC, etc)
    [LED Driver-NPTH.drl, LED Driver-PTH.drl, LED Driver.kicad_pcb, LED Driver.kicad_sch]
2023-05-31 Change LED terminal blocks to include fuse
    [din_rail_led.kicad_sch]
2023-05-31 Fix a disconnected SNS+ pin, generate new output files
    [LED Driver-B_Cu.gbl, LED Driver-B_Mask.gbs, LED Driver-B_Paste.gbp, LED Driver-B_Silkscreen.gbo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]
2023-07-19 Update sense resistor wiring for LED driver box, also aupdated PCB schematic to reflect the added resistor between out and V- on opamp
    [din_rail.kicad_sch, din_rail_led.kicad_sch, driver_pcb.kicad_sch, driver_pcbs.kicad_sch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]
2023-09-25 Working on digital IO box schematic drawing. Creating one sheet for internal connections between the arduinos and NI USB device
    [NI_DIO.kicad_sch, arduino_FIFO.kicad_sch, arduino_UTI.kicad_sch, arduino_clock.kicad_sch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]
2023-09-26 Finishing up all connections. Added DB9 for camera FSYN, and lemo for clock to CAEN
    [NI_DIO.kicad_sch, arduino_FIFO.kicad_sch, arduino_UTI.kicad_sch, arduino_clock.kicad_sch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]
2023-09-28 Added trigger first fault pins from FIFO arduino, and the LED/camera clock enable pins from clock arduino.
    [NI_DIO.kicad_sch, arduino_FIFO.kicad_sch, arduino_UTI.kicad_sch, arduino_clock.kicad_sch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]
2023-09-28 Added arrows to indicate input/output for relevant pins.
    [NI_DIO.kicad_sch, arduino_FIFO.kicad_sch, arduino_UTI.kicad_sch, arduino_clock.kicad_sch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]
2023-10-02 Added solidworks drawing for connector cutouts for CNC
    [171-009-103.STEP, 171-009-103.step.DXF, 171-009-103.step.SLDPRT, 171-015-103.DXF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]
2023-10-02 Added some drawings for DIO box cutouts
    [barrel assem_old.SLDASM, barrel assem_old.SLDPRT, barrel.SLDPRT, barrel_dio.SLDASM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]
2023-10-03 Added drawings for USB and ethernet cutouts
    [Eth connector.SLDPRT, USB connector.SLDPRT, dio cutouts.SLDDRW]
2023-10-04 Generate .PRT files from .ASM files. Then generate DXF files for CNC machining
    [ETH_in.DXF, ETH_mm.DXF, Eth connector.SLDPRT, USB connector.SLDPRT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]
2023-10-06 Change orientation of drawing
    [dio cutouts.SLDDRW]
2024-01-10 Schematic drawings for the piezo amplifying box, without detailed drawing of the amp PCB
    [back_panel.kicad_sch, front_panel.kicad_sch, piezo_amp_board.kicad_sch, piezo_amp_box.kicad_pcb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]
2024-03-06 Updated LED driver MOSFET part number, updated DIO box wirings as it's being made
    [din_rail.kicad_sch, din_rail_led.kicad_sch, driver_pcb.kicad_sch, led_driver_box.kicad_sch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]
2024-03-09 Modified DIO wiring, changed some NI USB and trigger pinouts
    [NI_DIO.kicad_sch, arduino_FIFO.kicad_sch, arduino_UTI.kicad_sch, arduino_clock.kicad_sch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]
2024-03-09 Clean up archive files
    [LED Driver.kicad_sch]
2024-05-20 Start schematic drawing for level shifter using optocoupler
    [level_shifter.kicad_pcb, level_shifter.kicad_sch, non-inverting-led.kicad_sch, non-inverting.kicad_sch]
2024-05-20 Replace design to use 847 instead of 817 so 4 channels per chip. Also removed the inverting logic version
    [level_shifter.kicad_sch]
2024-05-21 Change circuit so that while still non-inverting logic, the LED in optocoupler will only turn on when input is high
    [level_shifter.kicad_sch]
2024-05-21 Draw up first version of PCB board
    [level_shifter.kicad_pcb]
2024-05-21 minor changes, change mounting hole
    [level_shifter.kicad_pcb]
2024-05-21 minor changes
    [level_shifter.kicad_sch]
2024-06-03 Add 5V to 24V resistor values in another drawing
    [24v_to_5v.kicad_sch, level_shifter.kicad_pcb, level_shifter.kicad_sch]
2024-06-20 Start drawing the pizeo fuse box
    [amp_connectors.kicad_sch, front_panel.kicad_sch, piezo_connector.kicad_sch, piezo_fuse_box.kicad_pcb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]
2024-06-21 Add ch8 connectors, and fix pin directions
    [amp_connectors.kicad_sch, ch8_connectors.kicad_sch, front_panel.kicad_sch, piezo_connector.kicad_sch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]
2024-06-21 Add DIO and acoustics boxes for the wiring plot
    [acous_amp_box.kicad_sch, acous_fuse_box.kicad_sch, dio_box.kicad_sch, instrumentation_wiring.kicad_sch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]
2024-06-21 Draw gage and caen digitizers, switch, run control. Moved VJ feedthroughs to its own sheet
    [acous_amp_box.kicad_sch, acous_fuse_box.kicad_sch, caen.kicad_sch, gage_digitizer.kicad_sch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]
2024-07-10 Change level shifter resistance values
    [24v_to_5v.kicad_sch, level_shifter.kicad_sch]
2024-07-10 24v to 5v level shifter
2024-09-18 Add fire alarm and power connections in instrumentation wiring
    [DAQ_PC.kicad_sch, PLC_PC.kicad_sch, acous_amp_box.kicad_sch, acous_fuse_box.kicad_sch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]
2024-09-23 upload coupp piezo amp board drawing
2025-01-08 Change pin for fast compress trigger to PLC, also update to newer version of kicad
    [NI_DIO.kicad_sch, arduino_FIFO.kicad_sch, arduino_UTI.kicad_sch, arduino_clock.kicad_sch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]
2025-01-08 Update piezo amp box drawing to KiCad 8.0
    [back_panel.kicad_sch, front_panel.kicad_sch, piezo_amp_board.kicad_sch, piezo_amp_box.kicad_sch]
2025-01-08 Update led driver box drawing to KiCad 8.0
    [din_rail.kicad_sch, din_rail_led.kicad_sch, driver_pcb.kicad_sch, driver_pcbs.kicad_sch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]

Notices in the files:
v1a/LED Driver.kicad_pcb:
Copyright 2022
